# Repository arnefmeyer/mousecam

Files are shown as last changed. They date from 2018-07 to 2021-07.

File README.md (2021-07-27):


HitCount (http://hits.dwyl.io/arnefmeyer/mousecam)

# mousecam

(click [here](https://arnefmeyer.github.io/mousecam) for a html version)

<p align="center">
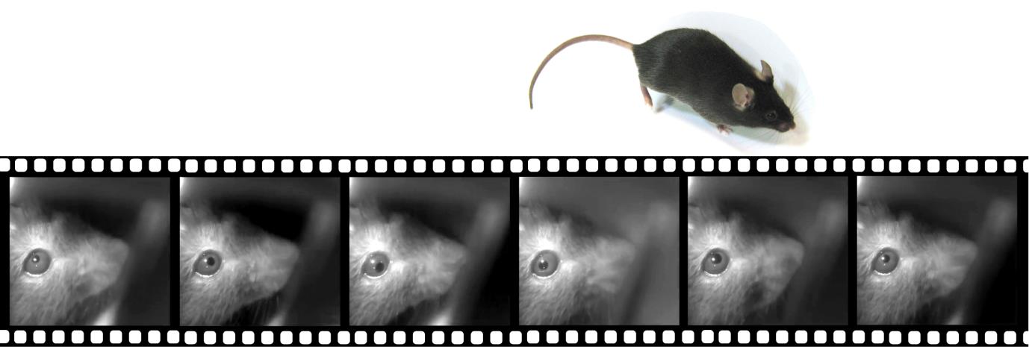
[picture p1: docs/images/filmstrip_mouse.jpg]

</p>

3D models and data extraction/analysis code for the head-mounted camera system described in:

>AF Meyer, J Poort, J O'Keefe, M Sahani, and JF Linden: _A head-mounted camera system integrates detailed behavioral monitoring with multichannel electrophysiology in freely moving mice_, Neuron, Volume 100, p46-60, 2018. [link (open access)](https://doi.org/10.1016/j.neuron.2018.09.020)

This repository contains the following:

* **mousecam**: a [Python package](https://github.com/arnefmeyer/mousecam/tree/master/mousecam) with functions for extracting and analyzing data recorded using the camera system, including
    - pupil fitting (including GUI)
    - body tracking (including GUI)
    - image registration (via fiji/imagej)
    - extraction of head orientation
* **parts**: [3D models](https://github.com/arnefmeyer/mousecam/tree/master/parts) (openscad/stl) and building instructions for the head-mounted camera system

## News

- 29/07/2021: Another paper using the mousecam published in [Nature Communications](https://www.nature.com/articles/s41467-021-24311-5)
- 08/06/2020: Paper on head and eye movements in freely moving mice published in [Current Biology](https://www.cell.com/current-biology/fulltext/S0960-9822(20)30556-X)
- 20/02/2020: New preprint using the mousecam on [bioRxiv](https://biorxiv.org/cgi/content/short/2020.02.20.957712v1)
- 21/11/2018: Add design files for [new camera module](https://github.com/arnefmeyer/mousecam/tree/master/parts)
- 04/11/18: This page is now also organized in a [website format](https://arnefmeyer.github.io/mousecam).
- 07/11/18: Added websites with step-by-step building instructions
- 28/11/18: The project is now on [open-ephys.org](http://www.open-ephys.org/mousecam/)
- 12/01/19: Added intructions on [how to remove IR filter from camera module](docs/building_instructions.md)
- 14/02/19: Mousecam featured on [openbehavior.com](https://edspace.american.edu/openbehavior/2019/02/06/head-mounted-camera-system/)

## Step-by-step building instructions

<p align="center">
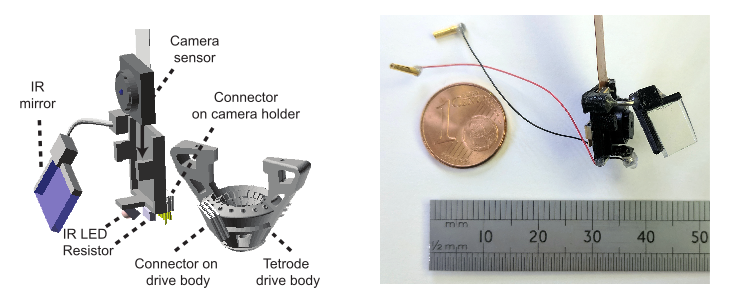
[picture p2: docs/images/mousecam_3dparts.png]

</p>

[1. Parts list](docs/parts_list.md)

[2. Building instructions](docs/building_instructions.md)

[3. Implantation](docs/implantation.md)

[4. Calibration](docs/calibration.md)

## Software

### Head-mounted camera code

[Custom camera software](https://github.com/arnefmeyer/RPiCameraPlugin) for the Raspberry Pi (RPi), which also integrates with the open-ephys plugin-GUI. As this software uses [zeromq](http://zeromq.org/) (with [bindings](http://zeromq.org/bindings:_start) for many programming languages) for communication between the recording computer and the RPi, it can easily be extended/adapted to other systems.

### Measurement of head orientation/movement data

Code (including open-ephys plugin) for reading data from intertia measurement unit (IMU) sensors and synchronizing movement data with neural recordings is available [here](https://github.com/arnefmeyer/IMUReaderPlugin).

### Behavioral segmentation

A Python package for behavioral scoring (including GUI for manual annotation) can be found [here](https://github.com/arnefmeyer/BehavioralScoring).

## Contribute

If you are looking for a different variant of the design or want to contribute modified and/or new designs, you can find all files in the [3D model directory](https://github.com/arnefmeyer/mousecam/tree/master/parts). Please use the *issue tracker* to report problems with building the camera system and create *pull requests* for improved/new designs.

- Issue Tracker: https://github.com/arnefmeyer/mousecam/issues
- Source Code: https://github.com/arnefmeyer/mousecam
- Project Website: https://arnefmeyer.github.io/mousecam

## References

```
@Article{Meyer2018,
  author    = {Meyer, Arne F. and Poort, Jasper and O’Keefe, John and Sahani, Maneesh and Linden, Jennifer F.},
  title     = {A Head-Mounted Camera System Integrates Detailed Behavioral Monitoring with Multichannel Electrophysiology in Freely Moving Mice},
  journal   = {Neuron},
  year      = {2018},
  volume    = {100},
  number    = {1},
  month     = oct,
  pages     = {46--60},
  issn      = {0896-6273},
  doi       = {10.1016/j.neuron.2018.09.020},
  url       = {https://doi.org/10.1016/j.neuron.2018.09.020},
  publisher = {Elsevier},
}

@Article{Meyer2020,
  author    = {Meyer, Arne F. and O'Keefe, John and Poort, Jasper},
  title     = {Two Distinct Types of Eye-Head Coupling in Freely Moving Mice},
  doi       = {10.1016/j.cub.2020.04.042},
  issn      = {0960-9822},
  number    = {11},
  pages     = {2116--2130},
  url       = {https://doi.org/10.1016/j.cub.2020.04.042},
  volume    = {30},
  comment   = {doi: 10.1016/j.cub.2020.04.042},
  journal   = {Current Biology},
  month     = jun,
  publisher = {Elsevier},
  year      = {2020},
}
```

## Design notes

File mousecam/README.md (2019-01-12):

# mousecam

A Python package containing data extraction and analysis code for the head-mounted camera system for freely moving mice (aka mousecam), e.g.,

* Pupil fitting code (including GUI)
* Body tracking code (including GUI)
* Extraction of dense optical flow (e.g., for whisker pad movement)
* Accelerometer analysis code (e.g., to extract head orientation)

## Dependencies

The package requires a number of other packages, e.g., [opencv](https://opencv.org/) (including dependencies) and [pyqtgraph](http://www.pyqtgraph.org/). It is recommended to use the [Anaconda Python distribution](https://www.anaconda.com/download/) and install all packages via conda, e.g., "conda install -c conda-forge opencv" from the command prompt.

## Installation

1. Install the package via "python setup.py install"
2. For building the Python extensions without installing the package: "python setup.py build_ext -i"

**Note:** The package contains a cython extension to wrap the image inpaint C++ code. However, installing extensions on Windows can be a bit tricky (see [here](https://blogs.msdn.microsoft.com/pythonengineering/2016/04/11/unable-to-find-vcvarsall-bat/) for details). If the extension cannot be built then the setup file will install the package without inpaint cython extension. In this case there will be some extra output (check lines with many exclamation marks).

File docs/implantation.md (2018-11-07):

# Implantation instructions

See paper for details on surgery. The counterpart of the miniature connector on the camera holder (e.g., Omnetics A79010-001 connector) can be fixed to the implant/microscope or directly onto the skull using strong dental cement (e.g., C&B Superbond, Sun Medical, Japan), so the camera holder can be easily and securely connected to the animal. The position and angle of the connector can be tested during surgery. However, it is possible to make finer adjustments later on by positioning the mirror (see [Calibration](calibration.md)). Therefore it is useful to be able to head-fix the mouse after it is fully recovered from surgery (e.g., in a recording set-up).

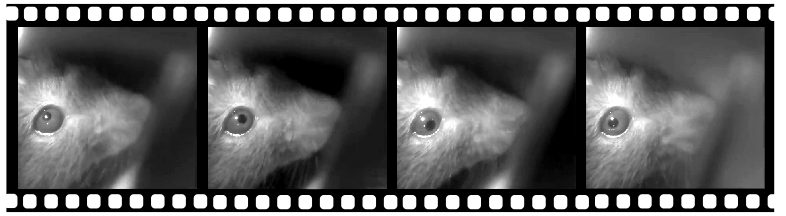
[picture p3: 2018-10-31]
docs/images/filmstrip.png

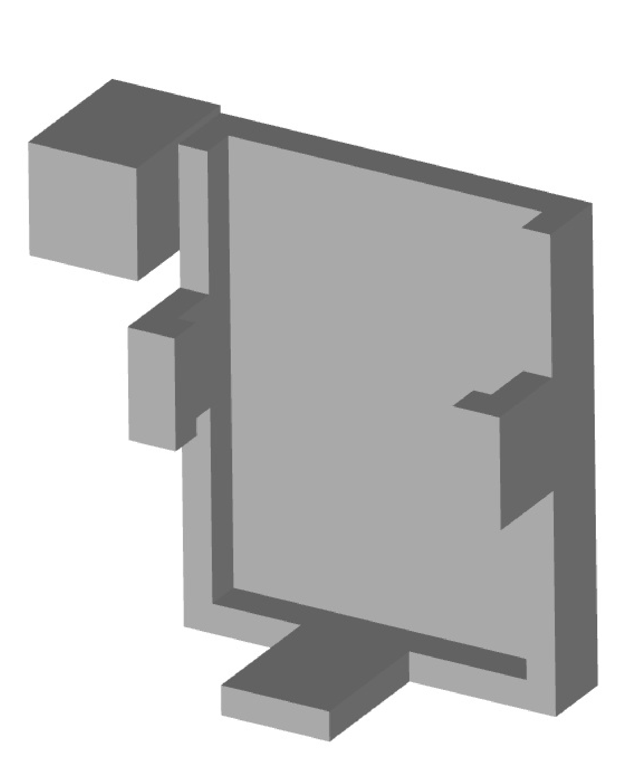
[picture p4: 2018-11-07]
docs/images/camholder_stl.png

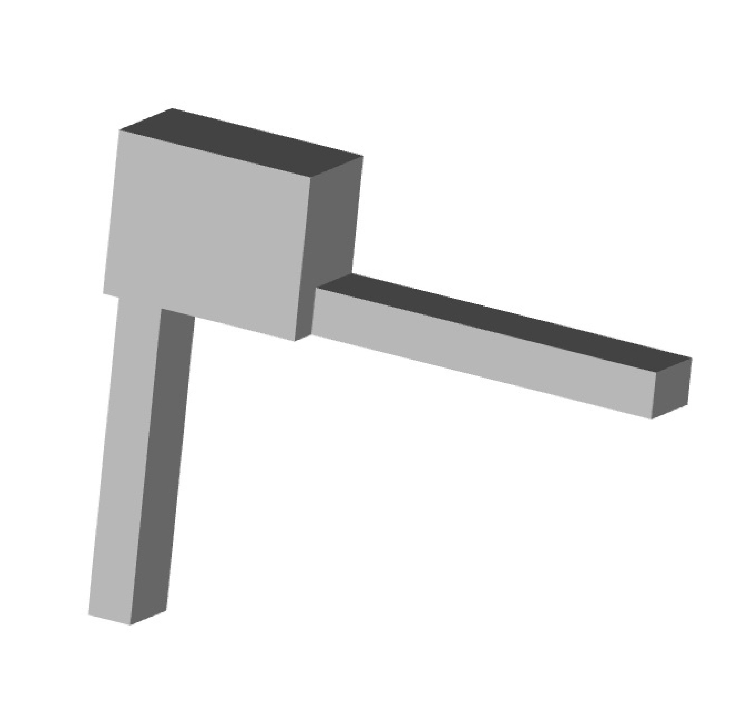
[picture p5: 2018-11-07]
docs/images/mirrorholder_stl.png

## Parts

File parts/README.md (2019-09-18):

# mousecam -- design files

<p align="center">

</p>

This folder contains design files (openscad/stl) and building instructions for the head-mounted camera system described in:

>AF Meyer, J Poort, J O'Keefe, M Sahani, and JF Linden: _A head-mounted camera system integrates detailed behavioral monitoring with multichannel electrophysiology in freely moving mice_, Neuron, Volume 100, p46-60, 2018. [link (open access)](https://doi.org/10.1016/j.neuron.2018.09.020)

**Note:** A newer version of the Adafruit 1937 module is available which is a big thicker (about 3.1 mm). Updated stl files (with suffix "_new_module.stl") can be found in the [stl folder](./stl).

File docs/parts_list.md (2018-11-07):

# Parts required for building the camera system

| **Part** | **Supplier/item** | **Weight(g)** | **Cost** | **Comment** |
| -------- | ----------------- | ------------- | -------- | ----------- |
Camera sensor | Adafruit 1937 | 0.51 | £33.00 | incl. suspended cable |
Camera holder | see [Custom parts](building_instructions.md) | 0.27 | n/a |
Mirror holder | see [Custom parts](building_instructions.md) | 0.07 | n/a |
IR mirror | Qioptiq Calflex-X | 0.15 | £4.00 | cut to 7 mm x 7 mm |
21 G steel cannula | Coopers Needle Works | 0.04 | £0.10 | cut to 20 mm |
IR LED | Vishay VSMB2943GX01 | 0.016 | £0.74 | |
Resistor (150--200) | Farnell Multicomp | 0.01 | £0.17 | package 3216 |
2 x 36 G wire | Alpha Wire 2936 | 2 x 0.01 | £0.10 | 50 mm |
2 x female gold pin | RS Components 481-500 | 2 x 0.05 | £0.90 | cut solder pot |
Miniature connector | Omnetics A79007-001 | 0.09 | £50.00 | cut thru-hole tails |
*Preci-Dip connector* | *852-10-008-10-001101* | *0.14* | *n/a* | *alternative to A79007-001* |

Weights were measured using a calibrated micro scale (Satorius CPA225D, Germany). Prices for steel cannula, mirror tiles, and wires were estimated without taking the cost of tools (e.g., glass cutter) into account. 3D printed parts were printed using a commercially available printer (Ultimaker 2+, the Netherlands) and PLA material (colorfabb, the Netherlands). Rows in italic indicate alternative parts.

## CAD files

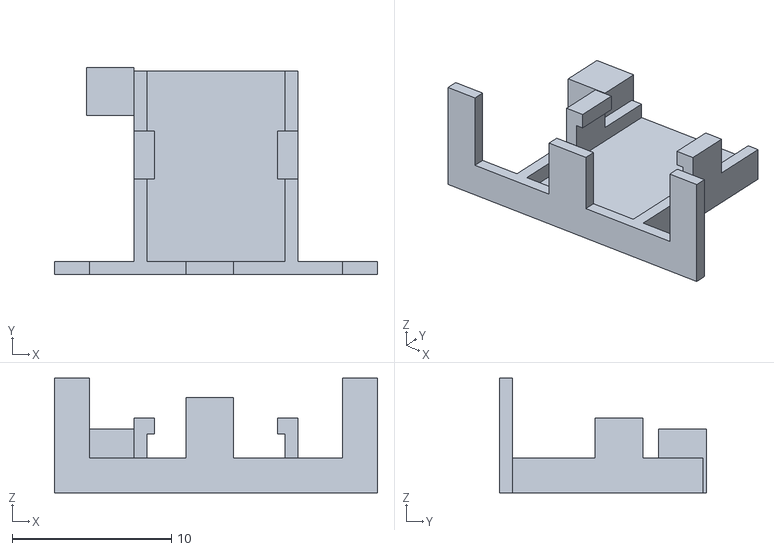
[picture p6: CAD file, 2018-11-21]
parts/stl/cam_holder_side_leds.stl
20.3 x 13.0 x 7.20

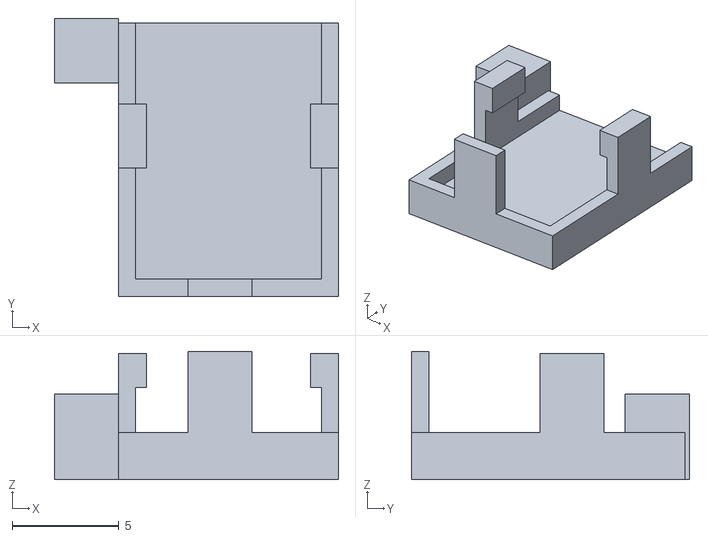
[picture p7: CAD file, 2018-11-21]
parts/stl/cam_holder_new_module.stl
13.3 x 13.0 x 6.00

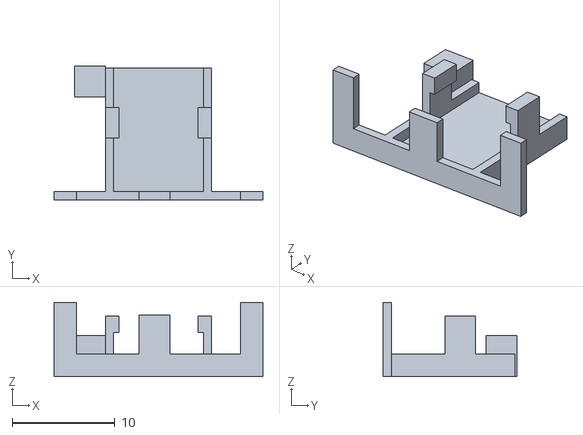
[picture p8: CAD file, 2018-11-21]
parts/stl/cam_holder_side_leds_new_module.stl
20.3 x 13.0 x 7.20

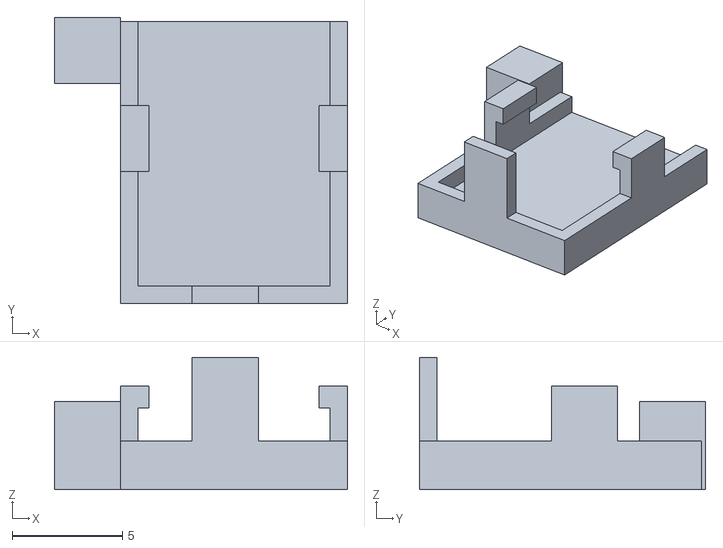
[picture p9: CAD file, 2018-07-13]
parts/stl/cam_holder.stl
13.3 x 13.0 x 6.00

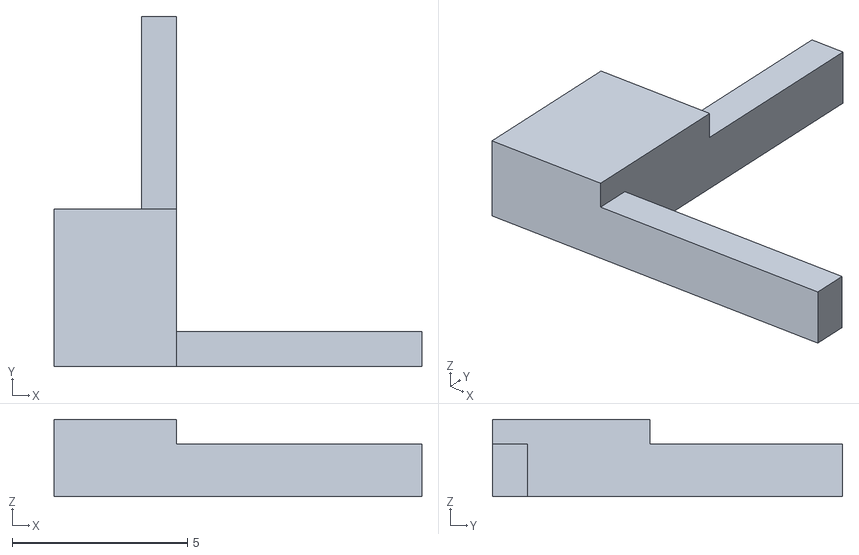
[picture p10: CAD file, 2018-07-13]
parts/stl/mirror_holder.stl
10.5 x 10.0 x 2.20

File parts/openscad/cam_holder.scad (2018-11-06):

/*
    Camera holder for the head-mounted camera system as described in:

    AF Meyer, J Poort, J O'Keefe, M Sahani, and JF Linden: A head-mounted 
    camera system integrates detailed behavioral monitoring with multichannel 
    electrophysiology in freely moving mice. Neuron, Volume 100, p46-60, 2018.

    Compatible with Omnivision OV5647-based (e.g., Adafruit 1937) and 
    comparable camera modules. Default dimensions:

    width = 8.5 mm
    height = 8.5 mm
    height_total = 11.8 mm (including electronics on cable)
    thickness = 2 mm

    author: arne.f.meyer@gmail.com
    licence: GPLv3
*/

// these are the dimensions of the holder, not the camera
width = 8.7;
height = 12;
thickness = 1.2;
depth = 1;
frame_width = 0.8;

// clips for holding the camera
clip_width = frame_width;
clip_height = 2.5;
clip_length = 3;
clip_dh = -.5;
clip_dw = .5;

// LED holder (bottom)
led_width = 3;
led_height = 4;

// block for the cannula that holds the mirror
mirrorblock_width = 3;
mirrorblock_height = 3;
mirrorblock_depth = 4;

// set to mirrorblock=true for making a hole for the cannula in the mirror 
// holder block (only recommended for 3D printers with very fine resolution)
mirrorblock_hole = false;
mirrorblock_hole_dia = 1;

$fn = 100;

union()
{
    // the holder for the camera (with frame)
    difference()
    {
        cube([width+2*frame_width, height+frame_width, thickness+depth], center=false);
        translate([frame_width, frame_width, thickness])
            cube([width, height+.1, depth+.1], center=false);
    }

    // clips for the camera
    translate([0, .5*height, thickness+depth])
        cube([clip_width, clip_length, clip_height-depth]);
    translate([0, .5*height, thickness+clip_height])
        cube([clip_width+clip_dw, clip_length, clip_height-depth+clip_dh]);

    translate([width+frame_width, .5*height, thickness+depth])
        cube([clip_width, clip_length, clip_height-depth]);
    translate([width+frame_width-clip_dw, .5*height, thickness+clip_height])
        cube([clip_width+clip_dw, clip_length, clip_height-depth+clip_dh]);

    // LED holder
    translate([.5*frame_width+.5*width-.5*led_width, 0, frame_width])
        cube([led_width, frame_width, thickness+led_height]);

    // block for the cannular holding the mirror
    translate([-mirrorblock_width, height - mirrorblock_height+depth, 0])
    {
        difference()
        {
            cube([mirrorblock_width, mirrorblock_height, mirrorblock_depth]);

            if (mirrorblock_hole)
            {
                translate([.5*mirrorblock_width, .5*mirrorblock_height, -.1])
                    cylinder(d=mirrorblock_hole_dia, h=mirrorblock_height+height+.2);
            }
        }
    }
}

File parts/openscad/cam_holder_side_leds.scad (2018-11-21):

/*
    Camera holder for the head-mounted camera system as described in:

    AF Meyer, J Poort, J O'Keefe, M Sahani, and JF Linden: A head-mounted 
    camera system integrates detailed behavioral monitoring with multichannel 
    electrophysiology in freely moving mice. Neuron, Volume 100, p46-60, 2018.

    Compatible with Omnivision OV5647-based (e.g., Adafruit 1937) and 
    comparable camera modules. Default dimensions:

    width = 8.5 mm
    height = 8.5 mm
    height_total = 11.8 mm (including electronics on cable)
    thickness = 2 mm

    Note:
    A newer version of the Adafruit 1937 module is available which is a big thicker
    (about 3.1 mm). Change clip_height below accordingly.

    author: arne.f.meyer@gmail.com
    licence: GPLv3
*/

// these are the dimensions of the holder, not the camera
width = 8.7;
height = 12;
thickness = 1.2;
depth = 1;
frame_width = 0.8;

// clips for holding the camera
clip_width = frame_width;
clip_height = 2.5;  // set to 3.1 for newer Adafruit 1937 module
clip_length = 3;
clip_dh = -.5;
clip_dw = .5;

// LED holder (bottom)
led_width = 3;
led_height = 4;

// LED holder (sides)
side_leds = true;
side_led_arm = 5;
side_led_dz = 5;

// block for the cannula that holds the mirror
mirrorblock_width = 3;
mirrorblock_height = 3;
mirrorblock_depth = 4;

// set to mirrorblock=true for making a hole for the cannula in the mirror 
// holder block (only recommended for 3D printers with very fine resolution)
mirrorblock_hole = false;
mirrorblock_hole_dia = 1;

$fn = 100;

union()
{
    // the holder for the camera (with frame)
    difference()
    {
        cube([width+2*frame_width, height+frame_width, thickness+depth], center=false);
        translate([frame_width, frame_width, thickness])
            cube([width, height+.1, depth+.1], center=false);
    }

    // clips for the camera
    translate([0, .5*height, thickness+depth])
        cube([clip_width, clip_length, clip_height-depth]);
    translate([0, .5*height, thickness+clip_height])
        cube([clip_width+clip_dw, clip_length, clip_height-depth+clip_dh]);

    translate([width+frame_width, .5*height, thickness+depth])
        cube([clip_width, clip_length, clip_height-depth]);
    translate([width+frame_width-clip_dw, .5*height, thickness+clip_height])
        cube([clip_width+clip_dw, clip_length, clip_height-depth+clip_dh]);

    // LED holder
    translate([.5*frame_width+.5*width-.5*led_width, 0, frame_width])
        cube([led_width, frame_width, thickness+led_height]);

    if (side_leds)
    {
        h = thickness+depth;
        translate([-side_led_arm, 0, 0])
        {
            cube([side_led_arm, frame_width, h]);
            translate([0, 0, h])
                cube([h, frame_width, side_led_dz]);
        }

        translate([width+2*frame_width, 0, 0])
        {
            cube([side_led_arm, frame_width, h]);
            translate([side_led_arm-h, 0, h])
                cube([h, frame_width, side_led_dz]);
        }
    }

    // block for the cannular holding the mirror
    translate([-mirrorblock_width, height - mirrorblock_height+depth, 0])
    {
        difference()
        {
            cube([mirrorblock_width, mirrorblock_height, mirrorblock_depth]);

            if (mirrorblock_hole)
            {
                translate([.5*mirrorblock_width, .5*mirrorblock_height, -.1])
                    cylinder(d=mirrorblock_hole_dia, h=mirrorblock_height+height+.2);
            }
        }
    }
}

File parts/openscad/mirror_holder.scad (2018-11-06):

/*
    Mirror holder for the head-mounted camera system as described in:

    AF Meyer, J Poort, J O'Keefe, M Sahani, and JF Linden: A head-mounted 
    camera system integrates detailed behavioral monitoring with multichannel 
    electrophysiology in freely moving mice. Neuron, Volume 100, p46-60, 2018.

    author: arne.f.meyer@gmail.com
    licence: GPLv3
*/

// base of the holder width hole for cannula
base_width = 3.5;
base_length = 4.5;
base_height = 2.2;  // suitable for 21 G cannulas

// "arms" for holding the IR mirror tile
arm_height = 1.5;
arm_width = 1;

// mirror dimensions; it might be useful to add 1-2 mm to both dimensions
// and cut off exceeding material using a scapel etc later on. Moreover, cut 
// mirror tiles are typically not perfect squares and for eye and whisker pad
// tracking it is typically useful to have a wide field of view in horizontal 
// rather than in vertical direction.
mirror_width = 7;
mirror_length = 9;

union()
{
    // base
    cube([base_width, base_length, base_height]);

    // left "arm"
    translate([base_width, 0, 0])
        cube([mirror_width, arm_width, arm_height]);

    // upper "arm"
    translate([base_width-arm_width, arm_width, 0])
        cube([arm_width, mirror_length, arm_height]);
}

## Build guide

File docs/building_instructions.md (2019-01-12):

# Building instructions

<p align="center">

</p>

## 1. Custom parts: camera and mirror holders

<p align="center">
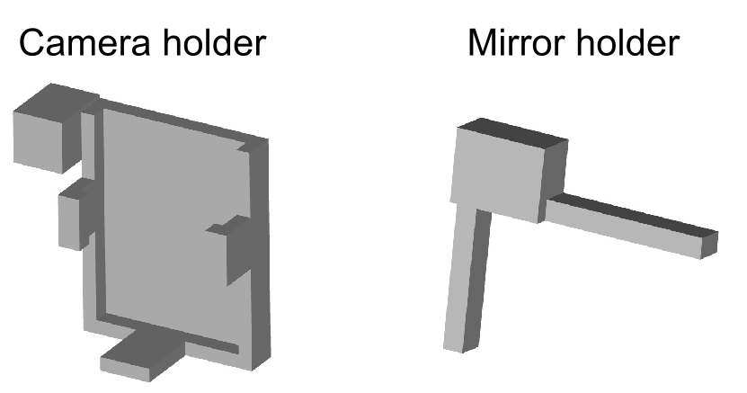
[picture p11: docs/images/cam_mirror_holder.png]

</p>

### Required tools and parts:

- 3D printer (e.g. Ultimaker 2)

- 3D printing material (e.g. Velleman PLA3B1)

- file, scalpel or other small knife

- camera holder STL file: [cam_holder.stl](./../parts/stl/cam_holder.stl)

- mirror holder STL file: [mirror_holder.stl](./../parts/stl/mirror_holder.stl)

Use the software for your 3D printer (e.g., Cura for Ultimaker) to
convert the STL files to a format your printer understands. After
printing clean up parts with file or scapel; try to fit camera into
holder (fit should be tight); and file side clips until camera fits in
holder.

Depending on the printer it might be useful to modify the designs such
that minimal filing/cutting is required after printing. A folder with 
source files (in [OpenSCAD](http://www.openscad.org/) format) is available 
in the mousecam repository in the same subdirectory as the STL file folder.

**Note:** A newer version of the Adafruit 1937 module is available which is a big thicker (about 3.1 mm). The below figure shows top and bottom views of the old an new camera modules. It seems that the main change is that some components were moved to the bottom of the module (see new module, bottom view). Updated STL files (with suffix "_new_module.stl") can be found in the [stl folder](./../parts/stl).

<p align="center">
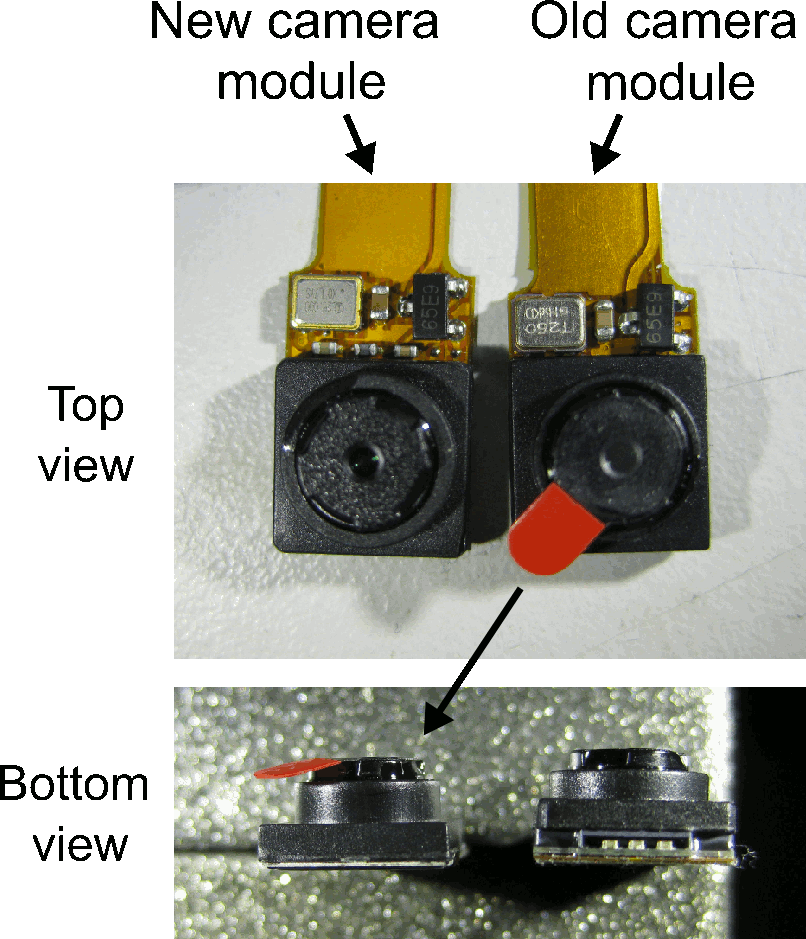
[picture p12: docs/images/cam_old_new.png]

</p>

## 2. Removal of the infrared filter

The camera module has an IR filter which needs to be removed when using IR light illumination. The filter is attached to the back of the lens. The lens can be removed by carefully turning it counter-clockwise with small pliers or big forcepts. Removing the lens will expose the camera sensor (see below picture, left). If possible avoid getting any dirst, dust etc on the camera sensor.

The IR filter is a thin round piece of glass (see below picture, middle) and can be removed by levering it off using a sharp knife (e.g., a scalpel blade) as indicated by the red arrow. It is possible to get it off in one single piece but if you break it don't worry -- just remove everything (e.g., using some air duster) and make sure the lens is clean (below picture, right).

<p align="center">
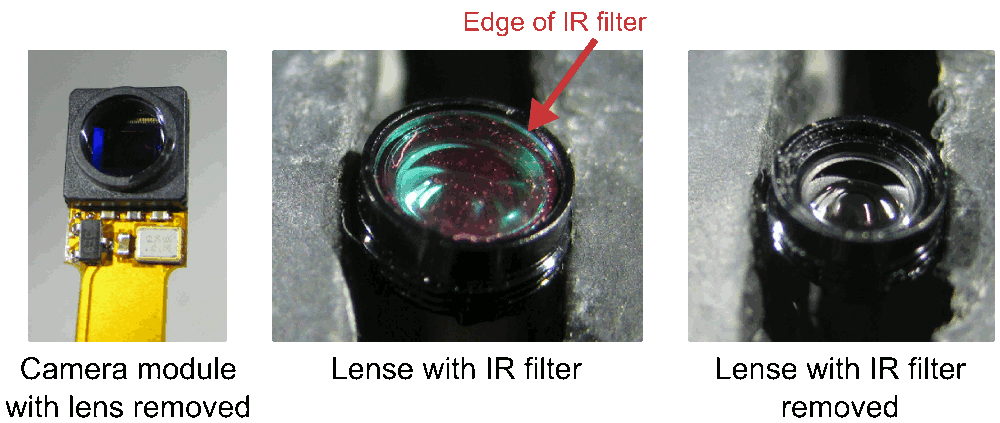
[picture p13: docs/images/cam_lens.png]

</p>

## 3. Assembling of the camera system

Note: construction of the camera system requires some off-the-shelf
parts. We provide example parts (supplier/item) as used in the above
paper but other parts might work as well.

### Required parts and tools:

-   Camera and mirror holders (see custom parts above)

-   21 G steel cannula (e.g., Coopers Needle Works). We successfully
    used thin-walled steel cannulas but other cannulas (e.g., a 21 G
    syringe needle after cutting the tip) will also work.

-   Infrared (IR) mirror (e.g., Qioptiq Calflex-X)

-   Small IR LED (e.g., Vishay VSMB2943GX01)

-   Small resistor, 150--200  (e.g., Farnell Multicomp, package 3216)

-   2 x 30--36 AWG wire (e.g., Alpha Wire 2936); length $\approx$ 5 cm

-   Miniature connectors for connecting the camera system to the
    implant/skull (e.g., Omnetics A79007-001/A79010-001 or 8-pin
    Mill-Max connectors)

-   optional: 2 x female gold pin (e.g., RS Components 481-500)

-   Dremel (e.g. Proxxon D-54518) with cutting disc (e.g. wheel no. 409)
    and 0.8 mm drill bit (DU68.10)

-   glass cutter; most glass cutters should work. We successfully used
    [this one](https://www.screwfix.com/p/vitrex-6-wheel-glass-cutter/10706).

-   2 combination pliers; if available 1 self-locking hemostat pliers

-   A length measuring device (e.g., ruler or caliper)

-   A thin and straight solid object, e.g., a metal ruler, for guiding
    glass cutter

### Steps:

<p align="center">
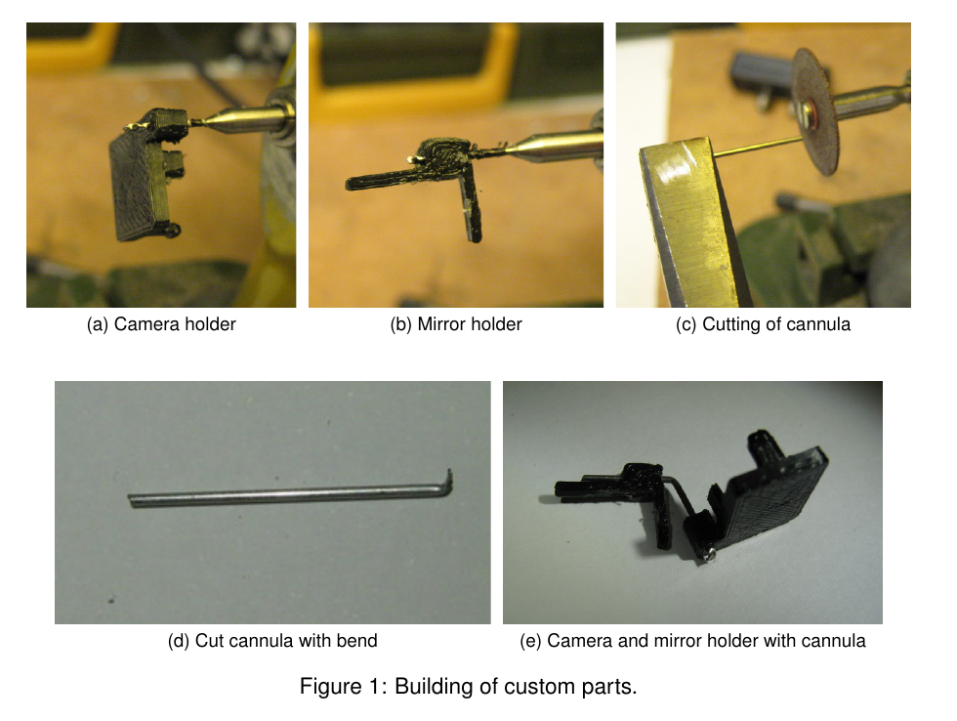
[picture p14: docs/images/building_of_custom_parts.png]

</p>

1.  Drill hole in the camera holder with Dremel and 0.8 mm drill bit
    (Figure 1a). Use hemostat or other pliers (not
    shown in photo) to hold the camera holder while drilling.

2.  Drill hole in the mirror holder (holding it with pliers) using
    Dremel and 0.8 mm drill bit     (Figure 1b).

3.  Cut cannula (21 G) to approx. 2 cm with cutting disc on Dremel
    (Figure 1c). Use safety glasses and hold both
    ends with pliers. Bend with second pliers at one of the ends to give
    sharp bent tip (Figure 1d). The bent tip will be fixed with
    a drop of epoxy to the back of the camera holder later on to prevent
    the mirror holder from rotating around the axis of the cannula.

4.  Push cannula from the back of the camera holder through the hole
    until the back of the camera holder hits the bent tip of the
    cannula.

5.  Bend cannula in the middle (approx. 1 cm) by about
    approx. 60&deg; using pliers. See Figure 1e) for a camera holder 
	with mirror holder and bent cannula.

6.  To cut the infrared (IR) mirror (e.g. Qioptiq Calflex-X 25 x 25 mm),
    first mark desired size (e.g., 7 x 7 mm for a relatively large
    field-of-view including eye and whiskers) with a removable marker.
    Score with glass cutter (along a thin solid object, e.g., a metal
    ruler) along one side of mirror. Break off scored line by holding
    both sides with pliers and carefully moving one pair up or down
    (wearing safety glasses). The mirror packing paper, a lens cleaning
    tissue, or some thin rubber sheet can be used to protect the mirror.
    Note: breaking glass is tricky and may occasionally result in a
    jagged edge; repeat until edge is satisfactory. Glue sharp side
    against mirror holder and cover outside with super glue or epoxy if
    necessary. It is also possible to use a file to get rid of sharp
    edges.

7.  Glue cut mirror tile to 3D printed mirror holder. A very thin layer
    of super glue (e.g., Loctite Power Flex Gel) is sufficient to
    permanently fix the mirror to the mirror holder.

8.  Put a very thin layer of super glue onto the cannula and gently push
    the cannula into the hole in the mirror holder. This will secure the
    mirror, but will still allow for positioning the mirror later on
    during calibration (see [Calibration](calibration.md)).

9.  Attach LED with a tiny drop of super glue to the bottom of the
    camera holder.

10. Solder a current-limiting resistor to the anode (+) of the LED
    (unless it is simpler to solder the LED closer to the power source).
    The value of the resistor depends on the LED and the power source
    (there are plenty of on-line tools, e.g., [this
    one](http://ledcalc.com/), to calculate the resistor value). Secure
    LED and resistor using a thin layer of (transparent) epoxy.

11. Solder two thin wires (30--36 AWG) to the cathode (-) of the LED and
    the resistor. The length of the wire depends on the distance between
    the camera holder and the LED power source. For the Intan headstage
    used in the paper about 5 cm wires were long enough. Moreover, in
    order to quickly connect/disconnect the wires to/from the power
    source during experiments it might be useful to use miniature gold
    pins and sockets. Cut away the solder pots, solder the wires to the
    pin sockets and secure the wires with a tiny drop of epoxy. Finally,
    solder the corresponding pins to the power source (e.g., the solder
    holes of the Intan headstage).

12. Fix connector (e.g., Omnetics A79007-001 after cutting away solder
    tails) using super glue to the back of the camera holder. See
    [Figure S1](https://www.cell.com/cms/10.1016/j.neuron.2018.09.020/attachment/0d7fad46-0021-44ca-ac57-d2f0a3dff074/mmc1.pdf) 
	in the [paper](https://www.cell.com/neuron/fulltext/S0896-6273(18)30822-5) 
	for an example of a fully assembled camera system with connector.

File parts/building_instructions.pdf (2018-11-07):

# Mousecam – a head-mounted camera system for freely moving mice

## Step-by-step building instructions

### Arne F. Meyer and Jasper Poort

### Last updated: November 7, 2018

## 1 Description

This document contains step-by-step building instructions for the head-mounted camera system described in:
Meyer AF∗

, Poort J∗
, O’Keefe J, Sahani M, Linden JF. A head-mounted camera system integrates detailed behavioral monitoring with multichannel electrophysiology in freely moving mice. (https://www.cell.com/neuron/fulltext/S0896-6273(18)30822-5) Neuron, Volume 100, p46-60, 2018.
(

∗ These authors contributed equally to this work)

If you are using the camera system in your work please cite the above paper.

Remarks: If you are looking for a different variant of the design or want to contribute modified and/or new designs, you can find all files in the mousecam github repository. (https://www.github.com/arnefmeyer/mousecam) Please use the issue tracker to report problems with building the camera system and create pull requests for improved/new designs.

Software: This guide describes the construction of the head-mounted camera system hardware. Running the system, synchronizing it with neural recordings, and extracting pupil position and other variables requires software. Examples include:

- Custom camera software (https://github.com/arnefmeyer/RPiCameraPlugin) for the Raspberry Pi (RPi), which also integrates with the open-ephys plugin-GUI. As this software uses zeromq (http://zeromq.org/) (with bindings (http://zeromq.org/bindings:_start) for many programming languages) for communication between the recording computer and the RPi, it can easily be extended/adapted to other systems.
- A Python package (https://github.com/arnefmeyer/mousecam/mousecam) with functions to do pupil tracking, body tracking, image registration, and estimation of head orientation from accelerometer data.
- Code (including open-ephys plugin) for controlling common inertia measurement unit (IMU) sensors and synchronizing movement data with neural recordings is available here. (https://github.com/arnefmeyer/IMUReaderPlugin)
- A Python package for behavioural scoring (including GUI for manual annotation) can be found here. (https://github.com/arnefmeyer/BehavioralScoring)

Detailed installation instructions can be found in the README.md files of the different repositories.

## 2 Parts required for building the camera system

Part | Supplier/item | Weight(g) Cost | Comment
Camera sensor | Adafruit 1937 | 0.51 | £33.00 incl. suspended
cable
Camera holder | see 3.1 | 0.27 | n/a
Mirror holder | see 3.1 | 0.07 | n/a
IR mirror | Qioptiq Calflex-X | 0.15 | £4.00 | cut to 7 mm x 7 mm
21 G steel cannula | Coopers Needle Works | 0.04 | £0.10 | cut to 20 mm
IR LED | Vishay VSMB2943GX01 | 0.016 | £0.74
Resistor (150–200Ω) Farnell Multicomp | 0.01 | £0.17 | package 3216
2 x 36 G wire | Alpha Wire 2936 | 2 x 0.01 | £0.10 | 50 mm
2 x female gold pin | RS Components 481-500 2 x 0.05 | £0.90 | cut solder pot
Miniature connector | Omnetics A79007-001 | 0.09 | £50.00 cut thru-hole tails
Preci-Dip connector | 852-10-008-10-001101 | 0.14 | | alternative to
| | | | A79007-001

Table 1: Parts required for building the miniature head-mounted camera system. Weights were measured using a calibrated micro scale (Satorius CPA225D, Germany). Prices for steel cannula, mirror tiles, and wires were estimated without taking the cost of tools (e.g., glass cutter) into account. 3D printed parts were printed using a commercially available printer (Ultimaker 2+, the Netherlands) and PLA material (colorfabb, the Netherlands). Gray rows indicate alternative parts.

## 3 Construction of the camera system

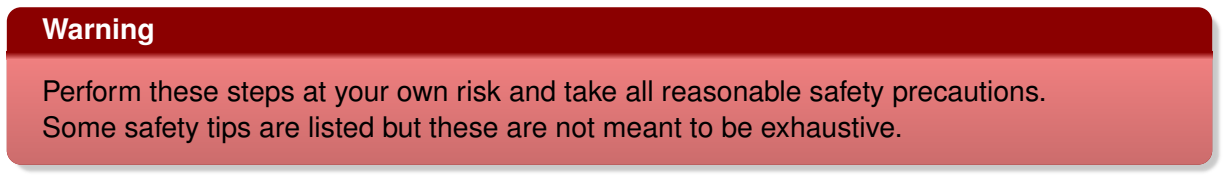
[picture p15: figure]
Warning

Perform these steps at your own risk and take all reasonable safety precautions. Some safety tips are listed but these are not meant to be exhaustive.

### 3.1 Custom parts: camera and mirror holders

Required tools and parts:

- 3D printer (e.g. Ultimaker 2)
- 3D printing material (e.g. Velleman PLA3B1)
- file, scalpel or other small knife
- camera holder STL file: cam_holder.stl (https://github.com/arnefmeyer/mousecam/tree/master/parts/stl/cam_holder.stl)
- mirror holder STL file: mirror_holder.stl (https://github.com/arnefmeyer/mousecam/tree/master/parts/stl/mirror_holder.stl)

Use the software for your 3D printer (e.g., Cura for Ultimaker) to convert the STL files to a format your printer understands. After printing clean up parts with file or scapel; try to fit camera into holder (fit should be tight); and file side clips until camera fits in holder.
Depending on the printer it might be useful to modify the designs such that minimal filing/cutting is required after printing. The source files (in OpenSCAD (http://www.openscad.org/) format) are available in the mousecam repository in the same directory as the STL files.

Camera holder

Mirror holder

### 3.2 Assembling of the camera system

Note: construction of the camera system requires some off-the-shelf parts. We provide example parts (supplier/item) as used in the above paper but other parts might work as well.

Required parts and tools:

- Camera and mirror holders (see 3.1)
- 21 G steel cannula (e.g., Coopers Needle Works). We successfully used thin-walled steel cannulas but other cannulas (e.g., a 21 G syringe needle after cutting the tip) will also work.
- Infrared (IR) mirror (e.g., Qioptiq Calflex-X)
- Small IR LED (e.g., Vishay VSMB2943GX01)
- Small resistor, 150–200 Ω (e.g., Farnell Multicomp, package 3216)
- 2 x 30–36 AWG wire (e.g., Alpha Wire 2936); length ≈ 5 cm
- Miniature connectors for connecting the camera system to the implant/skull (e.g., Omnetics A79007-001/A79010-001 or 8-pin Mill-Max connectors)

- optional: 2 x female gold pin (e.g., RS Components 481-500)
- Dremel (e.g. Proxxon D-54518) with cutting disc (e.g. wheel no. 409) and 0.8 mm drill bit (DU68.10)
- glass cutter; most glass cutters should work. We successfully used this one.
- 2 combination pliers; if available 1 self-locking hemostat pliers
- A length measuring device (e.g., ruler or caliper)
- A thin and straight solid object, e.g., a metal ruler, for guiding glass cutter

Steps:

1. Drill hole in the camera holder with Dremel and 0.8 mm drill bit (Figure 1a). Use hemostat or other pliers (not shown in photo) to hold the camera holder while drilling.
2. Drill hole in the mirror holder (holding it with pliers) using Dremel and 0.8 mm drill bit (Figure 1b).
3. Cut cannula (21 G) to ≈ 2 cm with cutting disc on Dremel (Figure 1c). Use safety glasses and hold both ends with pliers. Bend with second pliers at one of the ends to give sharp bent tip (Figure 1d). The bent tip will be fixed with a drop of epoxy to the back of the camera holder later on to prevent the mirror holder from rotating around the axis of the cannula.
4. Push cannula from the back of the camera holder through the hole until the back of the camera holder hits the bent tip of the cannula.
5. Bend cannula in the middle (≈ 1 cm) by about ≈ 60◦ using pliers. See Figure 1e for a camera holder with mirror holder and bent cannula.
6. To cut the infrared (IR) mirror (e.g. Qioptiq Calflex-X 25 x 25 mm), first mark desired size (e.g., 7 x 7 mm for a relatively large field-of-view including eye and whiskers) with a removable marker. Score with glass cutter (along a thin solid object, e.g., a metal ruler) along one side of mirror. Break off scored line by holding both sides with pliers and carefully moving one pair up or down (wearing safety glasses). The mirror packing paper, a lens cleaning tissue, or some thin rubber sheet can be used to protect the mirror. Note: breaking glass is tricky and may occasionally result in a jagged edge; repeat until edge is satisfactory. Glue sharp side against mirror holder and cover outside with super glue or epoxy if necessary. It is also possible to use a file to get rid of sharp edges.
7. Glue cut mirror tile to 3D printed mirror holder. A very thin layer of super glue (e.g., Loctite Power Flex Gel) is sufficient to permanently fix the mirror to the mirror holder.
8. Put a very thin layer of super glue onto the cannula and gently push the cannula into the hole in the mirror holder. This will secure the mirror, but will still allow for positioning the mirror later on during calibration (see 5).
9. Attach LED with a tiny drop of super glue to the bottom of the camera holder.
10. Solder a current-limiting resistor to the anode (+) of the LED (unless it is simpler to solder the LED closer to the power source). The value of the resistor depends on the LED and the power source (there are plenty of on-line tools, e.g., this one, (http://ledcalc.com/) to calculate the resistor value). Secure LED and resistor using a thin layer of (transparent) epoxy.

11. Solder two thin wires (30–36 AWG) to the cathode (-) of the LED and the resistor. The length of the wire depends on the distance between the camera holder and the LED power source. For the Intan headstage used in the paper about 5 cm wires were long enough. Moreover, in order to quickly connect/disconnect the wires to/from the power source during experiments it might be useful to use miniature gold pins and sockets. Cut away the solder pots, solder the wires to the pin sockets and secure the wires with a tiny drop of epoxy. Finally, solder the corresponding pins to the power source (e.g., the solder holes of the Intan headstage).
12. Fix connector (e.g., Omnetics A79007-001 after cutting away solder tails) using super glue to the back of the camera holder. See Figure S1 (https://www.cell.com/cms/10.1016/j.neuron.2018.09.020/attachment/0d7fad46-0021-44ca-ac57-d2f0a3dff074/mmc1.pdf) in the paper for an example of a fully assembled camera system with connector.

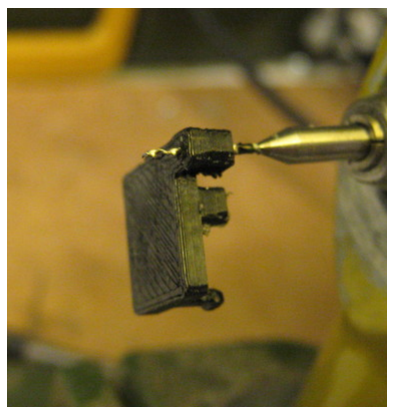
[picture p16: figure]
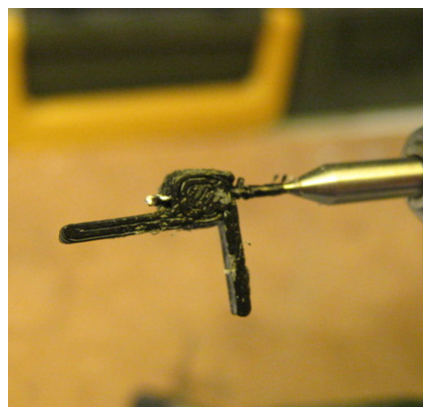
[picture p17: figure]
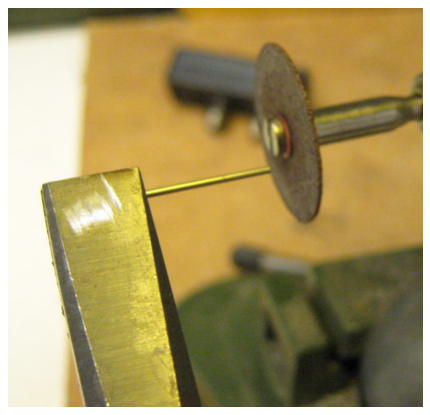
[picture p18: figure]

(a) Camera holder | (b) Mirror holder | (c) Cutting of cannula

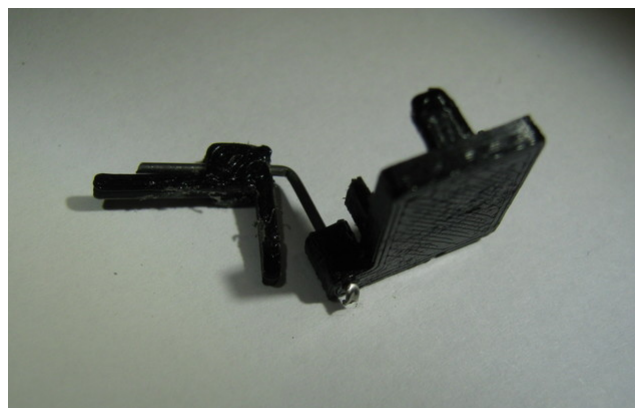
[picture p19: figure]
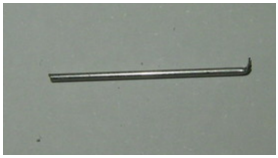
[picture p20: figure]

(d) Cut cannula with bend | (e) Camera and mirror holder with cannula

Figure 1: Building of custom parts.

## 4 Implantation instructions

See paper for details on surgery. The counterpart of the miniature connector on the camera holder (e.g., Omnetics A79010-001 connector) can be fixed to the implant/microscope or directly onto the skull using strong dental cement (e.g., C&B Superbond, Sun Medical, Japan), so the camera holder can be easily and securely connected to the animal. The position and angle of the connector can be tested during surgery. However, it is possible to make finer adjustments later on by positioning the mirror (see 5). Therefore it is useful to be able to head-fix the mouse after it is fully recovered from surgery (e.g., in a recording set-up).

## 5 Calibration

The easiest method is to head-fix the mouse and adjust the position of the mirror and the angle of the cannula while monitoring video images using the head-mounted camera. If the mirror holder is not tight enough (i.e. the mirror is slowly moving due to gravity) it is possible to add a very thin layer of super glue around the cannula to increase friction. This allows the mirror to be adjusted but it will stay in the right position. Once the mirror has been adjusted such that the camera shows the desired field of view, carefully take off the camera holder (without touching the mirror), and secure the mirror holder using strong epoxy (e.g., Araldite Steel). Do not glue the mirror holder while the camera system is on the head of the mouse! The LED angle may also need to be adjusted. It is also possible to calibrate the camera in a freely moving mouse, e.g., by restraining the mouse by hand, but this requires experience and is not recommended for those new to the camera system. Another option is to briefly anaesthetize the animal for adjusting the mirror.

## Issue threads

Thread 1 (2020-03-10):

### ISSUE TITLE
Discussion about tension in flex cable

### ISSUE THREAD

**Issue by banchan86** [arnefmeyer/mousecam#1]
Hi, just wanted to open a discussion about tension and how to resolve that. I haven't tested it out yet, but after building the device, seems like with a freely moving animal there will be a tension build up in the flex cable after it twists around for a while that might either impede movement or lead to damage in the cable. Just wondering what are your thoughts on it (will it not be too much of a problem, are there ways to resolve it, and how long can the mice be observed without relieving the tension by resetting the mice)

**Comment by arnefmeyer** [comment]
There is no risk of damaging the cable (at least for mice). Tension build up might occur when the cable twists around a couple of times but animals quickly "learn" to untwist the cable. Tension can be further reduced by extending the camera cable (e.g., https://shop.pimoroni.com/products/camera-cable-joiner-extender-for-raspberry-pi).

We have done recordings for more than an hour without manually untwisting the cable and did not observe any substantial differences in behavior compared to mice without camera. Of course, this depends on the behavior you want to study. If the behavior involves a lot of rotations in one direction you might consider attaching the whole raspberry pi to a slip ring commutator so it can rotate with the animal. Power and trigger signals (3 wires) could simply be transmitted using the commutator.

note that we are working on a newer version of the camera with much thinner cable but this will take some more time.

**Comment by banchan86** [comment]
Hey arne thanks! mounting the raspberry pi on a slip ring commutator sounds promising

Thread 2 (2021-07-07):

### ISSUE TITLE
IR filter in new Pi cameras

### ISSUE THREAD

**Issue by apaks** [arnefmeyer/mousecam#2]
Hello,

First, thanks for such a detailed instructions on building the implant.

I was wondering whether you tried to remove IR filter from the new Pi cameras. I was not able to locate it (see pictures below). However, I tried to remove the lens and it makes images brighter under IR illumination but not enough to record good quality videos. 

Also, did you try to use red LED to illuminate mouse eyes? 

Thanks,

![20210630_201717](https://user-images.githubusercontent.com/18731254/124184013-fd97f800-da86-11eb-97af-9a0f83a2aa03.jpg)
![20210630_202359](https://user-images.githubusercontent.com/18731254/124184016-fd97f800-da86-11eb-86c9-9225768430ae.jpg)

**Comment by arnefmeyer** [comment]
In some newer camera modules, the IR filter is glued on top of the CMOS sensor. Not sure if it is possible to remove the filter without damaging the sensor. However, arducam is selling a similar camera module without IR filter:
https://www.arducam.com/product/1-4-5-noir-mpspy-camera-module-sensor-flex-cable-raspberry-pi/

**Comment by apaks** [comment]
Thanks for the reply, I will try arducam cameras.

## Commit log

2018-05-10 add py3 compat print statements
2018-07-13 add design files and building instructions
    [camholder.scad, camholder.stl, mirrorholder.scad, mirrorholder.stl]
2018-11-06 update readme and refs
    [camholder.scad, mirrorholder.scad]
2018-11-07 add websites with building instructions
    [cam_holder.scad, cam_holder.stl, mirror_holder.scad, mirror_holder.stl]
2018-11-21 add design files for new camera module
    [cam_holder_new_module.stl, cam_holder_side_leds.scad, cam_holder_side_leds.stl, cam_holder_side_leds_new_module.stl]
2019-05-28 add fallback to get correct frame count

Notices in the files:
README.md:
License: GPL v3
